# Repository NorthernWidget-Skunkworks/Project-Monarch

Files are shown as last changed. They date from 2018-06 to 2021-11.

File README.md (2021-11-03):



# Project-Monarch
Designs for a small scale and low cost pyronometer operating in both the short wave and long wave spectral regions

## Millable components

* [Pipe mount](https://easel.inventables.com/projects/cAirZefIUws53oghGYYopw). Accepts 1.25" to 3.25" innner diameter (ID) 1/4" (bolt diameter) U bolts. (1 1/8" U bolts are possible if you're willing to bend them.) Typical sizes available in the USA are 1.25", 1.5", 1.75", and 2".
* [Drilling jig](https://easel.inventables.com/projects/s-fOn9DWTmkeizO0vO8MGw) for Monarch box`

<br>
<br />This work is licensed under a <a rel="license" href="http://creativecommons.org/licenses/by-sa/4.0/">Creative Commons Attribution-ShareAlike 4.0 International License</a>.

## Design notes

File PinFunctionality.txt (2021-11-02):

Pin Functionality Monarch Short-Wave

Pin		Function
D0		Lux Int, Active Low
D1		Adc Int, Active Low
D7		Slave Address Select 
D3		Software SCL
D2		Software SDA

Function Explanation:

Lux Int:
Lux sensor (VEML6030) can be configured to output an interrupt for certian situations, this pin is native high (pull up), and it pulled low by the Lux sensor if an interrupt is triggered. Interrupt trigger must be configured by user.

Adc Int:				
ADC (ADS1115) can be configured to output an interrupt for certian situations, this pin is native high (pull up), and it pulled low by the ADC sensor if an interrupt is triggered (generally used to indicate a finished conversion). Interrupt trigger must be configured by user.

Slave Address Select:
This pin is used to select I2C device (if the device is the "top" or "bottom" device). This pin must be pulled up internally, and is natively floating (can be pulled up internally). This pin is an input, when the solder jumper on the board (J1) is jumped, this pin is pulled low, indicating the alternate device address should be used.

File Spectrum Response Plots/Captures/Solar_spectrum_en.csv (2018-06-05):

x | Curve1
204.85 | 0.1295
216.07 | 0.18429
225.9 | 0.23908
234.31 | 0.29387
242.73 | 0.34866
249.75 | 0.40574
255.36 | 0.46053
262.38 | 0.51761
269.39 | 0.5724
276.41 | 0.62948
282.02 | 0.68655
287.63 | 0.74135
294.65 | 0.79842
300.26 | 0.85322
307.27 | 0.91029
312.89 | 0.96737
319.9 | 1.02216
325.51 | 1.07924
332.53 | 1.13403
339.54 | 1.19111
346.56 | 1.2459
353.57 | 1.30298
360.59 | 1.35777
369.01 | 1.41256
377.43 | 1.46964
387.25 | 1.52443
398.47 | 1.5952
402.68 | 1.62716
412.5 | 1.64998
426.53 | 1.7002
439.16 | 1.73215
458.8 | 1.77779
486.87 | 1.80973
519.14 | 1.80741
531.76 | 1.79597
558.42 | 1.76169
582.27 | 1.71828
603.32 | 1.67258
622.96 | 1.62689
660.85 | 1.53095
679.09 | 1.48297
712.76 | 1.3916
731 | 1.34363
747.84 | 1.29565
766.08 | 1.24768
784.32 | 1.19971
798.38 | 1.16441
815.62 | 1.11836
836.39 | 1.07159
852.74 | 1.02698
870.86 | 0.99171
888.14 | 0.9507
910.59 | 0.90728
933.04 | 0.86159
955.49 | 0.81818
979.34 | 0.77705
996.18 | 0.74735
1020.03 | 0.70622
1045.29 | 0.66737
1071.94 | 0.62852
1097.2 | 0.59195
1111.23 | 0.57367
1137.89 | 0.53939
1167.35 | 0.5051
1196.82 | 0.47538
1226.28 | 0.44566
1255.75 | 0.41594
1288.02 | 0.39079
1318.88 | 0.36335
1351.15 | 0.34048
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

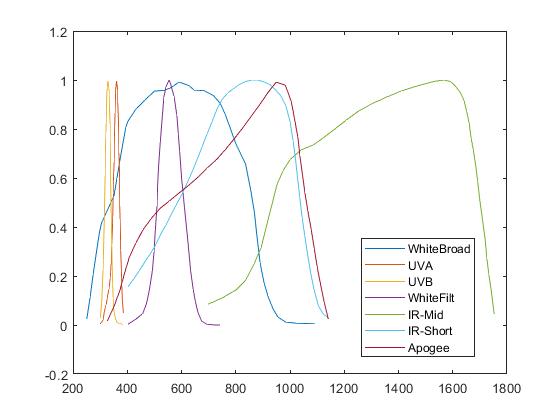
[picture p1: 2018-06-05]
Spectrum Response Plots/Spectrum.jpg

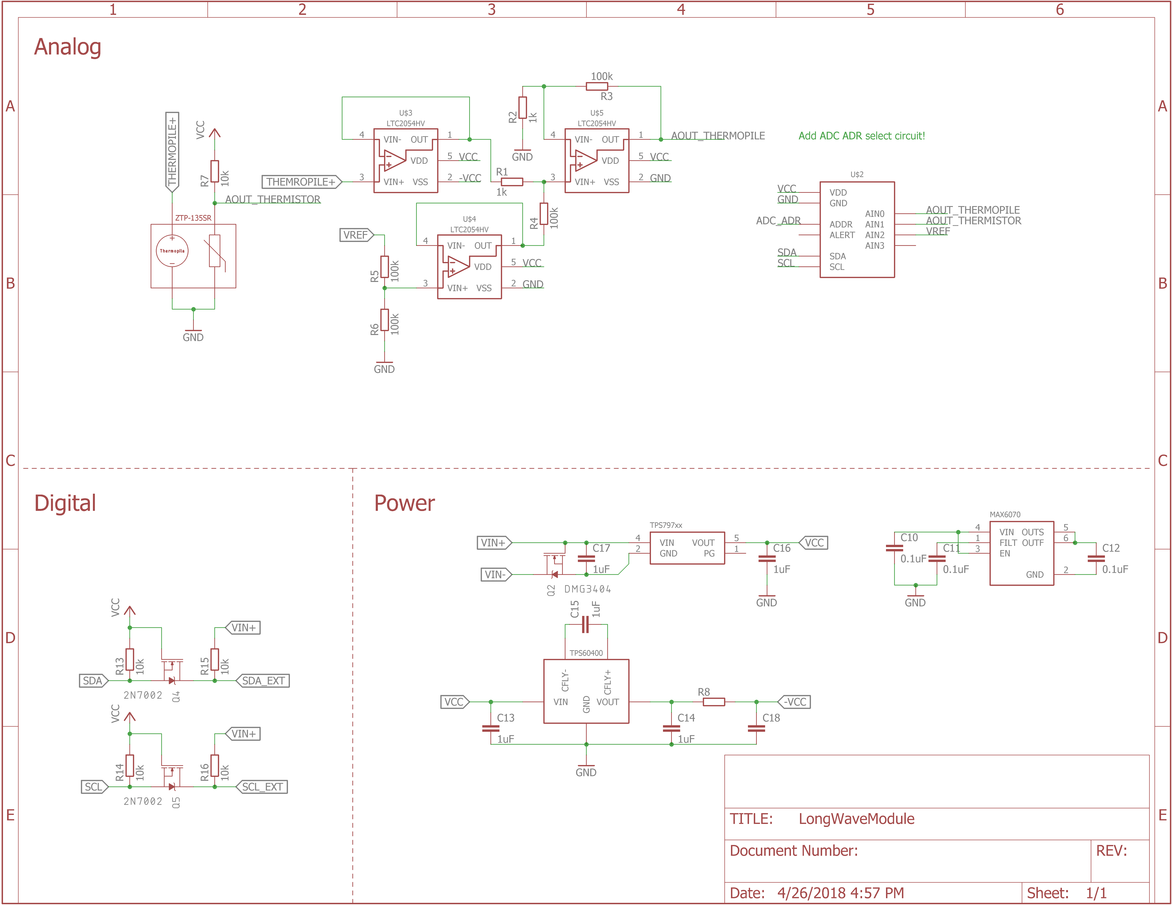
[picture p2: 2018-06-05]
Hardware/LongWaveSch.png

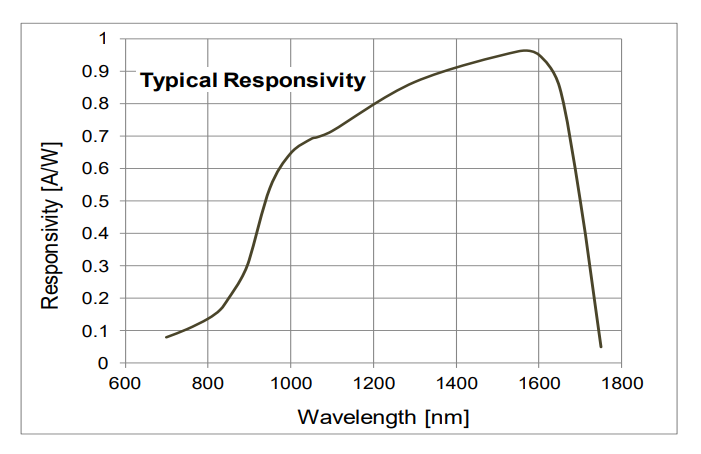
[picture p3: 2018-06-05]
Spectrum Response Plots/Captures/IR_MidWave_Response.png

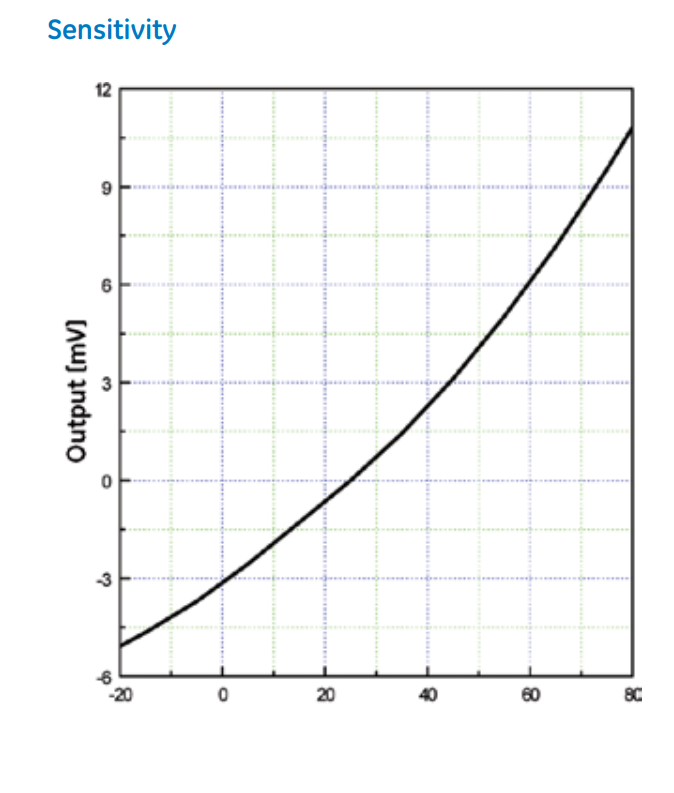
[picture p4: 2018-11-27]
Spectrum Response Plots/Captures/ZTP-135_Response.png

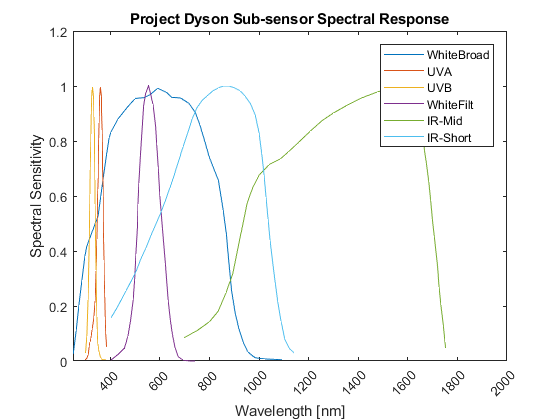
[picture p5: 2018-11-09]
Spectrum Response Plots/Spectrum.png

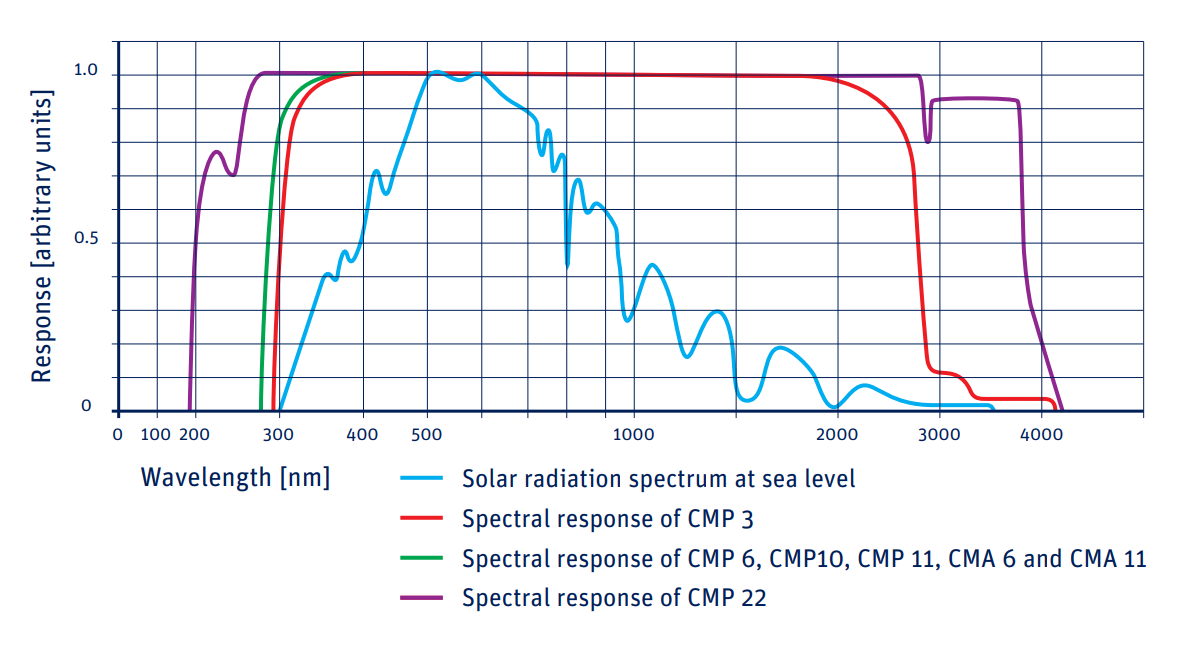
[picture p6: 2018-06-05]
Spectrum Response Plots/Captures/KippAndZonen_Response.png

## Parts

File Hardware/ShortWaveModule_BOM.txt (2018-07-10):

Partlist exported from C:/Users/You/Documents/Project-Dyson/Hardware/ShortWaveModule_SmallBoard.sch at 7/9/2018 9:44 AM

Qty Value                   Device                  Package              Parts                                         Description                                                                          DIGIKEY                DISP    MF                  MPN                PROD_ID     VALUE   VALUE_PART
2                           MOUNTING_HOLE4_NP       4_40                 H1, H2                                        Genaric Mechanical Mounting Hole                                                                                                                                                         
2   0.15uF                  C-EU0.15UFC0603         C0603                C2, C3                                        CAPACITOR, European symbol                                                           732-7990-1-ND                  Wurth               885012206072                                     
8   0.1uF                   C-EU0.1UFC0603          C0603                C4, C5, C8, C9, C10, C11, C12, C14            CAPACITOR, European symbol                                                           490-6051-1-ND                  Murata              GCM188R71E104KA57D                               
1   100k                    R-EU_P100KR0603         R0603                R4                                            RESISTOR, European symbol                                                            P100KDBCT-ND                   Panasonic           ERA-3AEB104V                           100k      
10  10k                     R-EU_10KR0603           R0603                R6, R7, R8, R11, R12, R13, R14, R15, R16, R18 RESISTOR, European symbol                                                            P10.0KHCT-ND                   Panasonic           ERJ-3EKF1002V                          10k       
1   10k                     R-EU_P10KR0603          R0603                R17                                           RESISTOR, European symbol                                                            P10KDBCT-ND                    Panasonic           ERA-3AEB103V                           10k       
1   10k                     R-EU_P10KR0603          R0603                R5                                            RESISTOR, European symbol                                                            P10KDBCT-ND                    Panasonic           ERA-3AEB103V                           10k       
1   10k                     THERMISTOR10K           R0603                RT1                                           Thermistor                                                                           490-16279-1-ND                 Murata              NCU18XH103F60RB                                  
1   10uF                    C-EU10UFC0805           C0805                C1                                            CAPACITOR, European symbol                                                           490-6473-6-ND                  Murata              GRM21BR61C106KE15K                               
4   1k                      R-EU_P1KR0603           R0603                R1, R2, R9, R10                               RESISTOR, European symbol                                                            P1.0KDBCT-ND                   Panasonic           ERA-3AEB102V                           1k        
4   1uF                     C-EU1UFC0603            C0603                C6, C7, C13, C15                              CAPACITOR, European symbol                                                           1276-6524-1-ND                 Samsung             1276-6524-1-ND                                   
1   27R                     R-EU_27R0603            R0603                R3                                            RESISTOR, European symbol                                                            311-27.0HRCT-ND                Yageo               RC0603FR-0727RL                        27        
2   2N7002                  MOSFET-NCH-2N7002PW     SOT323               Q1, Q2                                        N-channel MOSFETs                                                                    2N7002W-FDICT-ND               Diodes Incorporated 2N7002W-7-F        TRANS-11151 2N7002            
1   ADS1115                 ADS1115                 VSSOP_10             U5                                            ADS1115 - Sigma Delta ADC                                                            296-38849-1-ND                 TI                  ADS1115IDGSR                                     
1   ADXL343                 ADXL343                 LGA-14               U1                                            ADXL343 - Digital Accelerometer(I2C/SPI)                                             ADXL343BCCZ-ND                 Analog Devices      ADXL343BCCZ                                      
1   ATTINY441/841841        ATTINY441/841841        SOIC_14              U2                                            ATTINY441, ATTINY841 8 bit MCU, 4/8k flash, 256/512B SRAM                            ATTINY841-SSU-ND               Atmel               ATTINY841-SSU                                    
1   AVRISP-6                AVRISP-6                AVRISP               ISP1                                          AVR ISP HEADER                                                                                                                                                                           
3   CONN_42.54              CONN_42.54              1X04                 J2, J3, J4                                    Genaric 4 pin connector                                                                                                                                                                  
1   CONN_42.54_SCREW        CONN_42.54_SCREW        1X04_SCREW           J1                                            Genaric 4 pin connector                                                              ED10563-ND                     On Shore            OSTVN04A150                                      
1   DMG3404                 MOSFET-NCH-DMG3404L     SOT23-3              Q3                                            N-channel MOSFETs                                                                    DMG3404L-7DICT-ND              Diodes Incorporated DMG3404L-7                     DMG3404           
2   JUMPER-SMT_2_NO_SILK    JUMPER-SMT_2_NO_SILK    SMT-JUMPER_2_NO_SILK JP1, JP2                                      Normally open jumper                                                                                                                                                                     
2   LTC2054                 LTC2054                 SOT23-5              U3, U4                                        LTC2054 -Single Micropower Zero Drift Op-Amp                                         LTC2054HS5#TRMPBFCT-ND LTC2054 LT                  LTC2054HS5#TRMPBF                                
1   PHOTODIODESD003-151-001 PHOTODIODESD003-151-001 D1206                D1                                            Photodiode                                                                           SD003-151-001CT-ND             Luna Opto           SD003-151-001                                    
1   PHOTODIODEVEMD1060      PHOTODIODEVEMD1060      D0805                D2                                            Photodiode                                                                           VEMD1060X01CT-ND               Vishay              VEMD1060X01                                      
1   TPS79733                TPS79733                DCK_R-PDSO-G5        U6                                            TPS797xx, Ultra low power linear voltage regulator, fixed voltages of 1.8v, 3v, 3.3v 296-11990-1-ND                 TI                  TPS79733DCKR                                     
1   VEML6030                VEML6030                VEML6030             U7                                            VEML6030 - Ambient Light Sensor with I2C Interface                                   VEML6030-GS15CT-ND             Vishay              VEML6030-GS15                                    
1   VEML6075                VEML6075                VEML6075             U8                                            VEML6075 - UVA and UVB Light Sensor with I2C Interface                               VEML6075CT-ND                  Vishay              VEML6075

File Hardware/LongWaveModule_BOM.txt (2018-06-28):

Partlist exported from C:/Users/You/Documents/Project-Dyson/Hardware/LongWaveModule.sch at 6/28/2018 1:53 PM

Qty Value                        Device                       Package                      Parts                          Description                                                                          DIGIKEY                 DISP      MF                  MPN                PROD_ID     VALUE   VALUE_PART
7   0.1uF                        C-EU0.1UFC0603               C0603                        C5, C6, C9, C10, C11, C12, C13 CAPACITOR, European symbol                                                           490-6051-1-ND                     Murata              GCM188R71E104KA57D                               
4   100k                         R-EU_P100KR0603              R0603                        R6, R7, R10, R11               RESISTOR, European symbol                                                            P100KDBCT-ND                      Panasonic           ERA-3AEB104V                           100k      
4   10k                          R-EU_10KR0603                R0603                        R1, R2, R4, R5                 RESISTOR, European symbol                                                            P10.0KHCT-ND                      Panasonic           ERJ-3EKF1002V                          10k       
1   10k                          R-EU_P10KR0603               R0603                        R3                             RESISTOR, European symbol                                                            P10KDBCT-ND                       Panasonic           ERA-3AEB103V                           10k       
1   1k                           R-EU_1KR0603                 R0603                        R12                            RESISTOR, European symbol                                                            311-1KLDCT-ND                     Yageo               AC0603FR-071KL                         1k        
2   1k                           R-EU_P1KR0603                R0603                        R8, R9                         RESISTOR, European symbol                                                            P1.0KDBCT-ND                      Panasonic           ERA-3AEB102V                           1k        
6   1uF                          C-EU1UFC0603                 C0603                        C1, C2, C3, C4, C7, C8         CAPACITOR, European symbol                                                           1276-6524-1-ND                    Samsung             1276-6524-1-ND                                   
3   2-56                         MOUNTING_HOLE2_NP            2_56                         H1, H2, H3                     Genaric Mechanical Mounting Hole                                                                                                                                                            
2   2N7002                       MOSFET-NCH-2N7002PW          SOT323                       Q1, Q2                         N-channel MOSFETs                                                                    2N7002W-FDICT-ND                  Diodes Incorporated 2N7002W-7-F        TRANS-11151 2N7002            
1   ADS1115                      ADS1115                      VSSOP_10                     U7                             ADS1115 - Sigma Delta ADC                                                            296-38849-1-ND                    TI                  ADS1115IDGSR                                     
1   CONN_42.54_SCREW             CONN_42.54_SCREW             1X04_SCREW                   J1                             Genaric 4 pin connector                                                              ED10563-ND                        On Shore            OSTVN04A150                                      
1   DMG3404                      MOSFET-NCH-DMG3404L          SOT23-3                      Q3                             N-channel MOSFETs                                                                    DMG3404L-7DICT-ND                 Diodes Incorporated DMG3404L-7                     DMG3404           
1   JUMPER-SMT_3_1-NC_PASTE_SILK JUMPER-SMT_3_1-NC_PASTE_SILK SMT-JUMPER_3_1-NC_PASTE_SILK JP1                            Normally closed solder jumper (1 of 2 connections)                                                                                                                                          
1   LTC2050HV                    LTC2050HV                    SOT23-5                      U2                             LTC2050 -Single Micropower Zero Drift Op-Amp                                         LTC2050HVIS5#TRPBFCT-ND LTC2050HV LT                  LTC2050HVIS5#TRPBF                               
2   LTC2054                      LTC2054                      SOT23-5                      U3, U4                         LTC2054 -Single Micropower Zero Drift Op-Amp                                         LTC2054HS5#TRMPBFCT-ND  LTC2054   LT                  LTC2054HS5#TRMPBF                                
1   MAX6070AAUT18                MAX6070AAUT18                SOT23-6L                     U8                             MAX6070 Low Noise high precision voltage referance                                   MAX6070BAUT18+TCT-ND              Maxim               MAX6070BAUT18+T                                  
1   STP-135SR                    STP-135SR                    TO-46                        U1                             ZTP-135SR - Thermopile Temp Sensor with integrated thermistor                        235-1330-ND                       Amphenol            ZTP-135SR                                        
1   TPS60403                     TPS60403                     SOT23-5                      U5                             TPS6040x - Unregulated Charge Pump Voltage Inverter                                  296-27005-1-ND                    TI                  TPS60403DBVR                                     
1   TPS79733                     TPS79733                     DCK_R-PDSO-G5                U6                             TPS797xx, Ultra low power linear voltage regulator, fixed voltages of 1.8v, 3v, 3.3v 296-11990-1-ND                    TI                  TPS79733DCKR

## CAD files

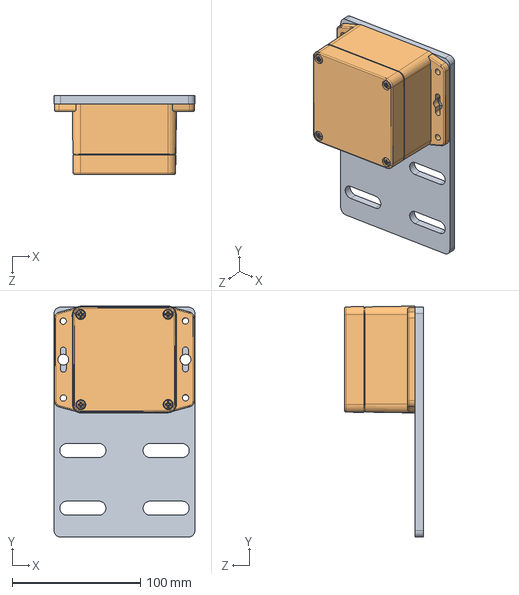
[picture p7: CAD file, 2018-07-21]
PipeMount.SLDASM
110.0 x 180.3 x 61.5 mm
PipeMount
W_-31F1

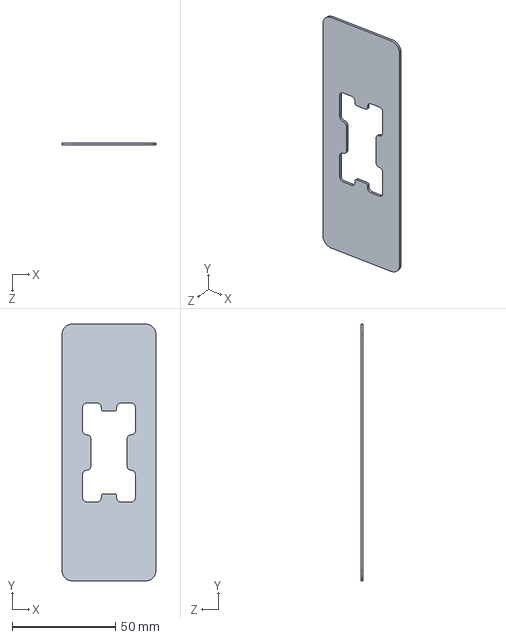
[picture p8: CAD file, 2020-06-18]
3Dprint/StencilMount_MonarchLW.SLDPRT
45.5 x 124.4 x 1.20 mm

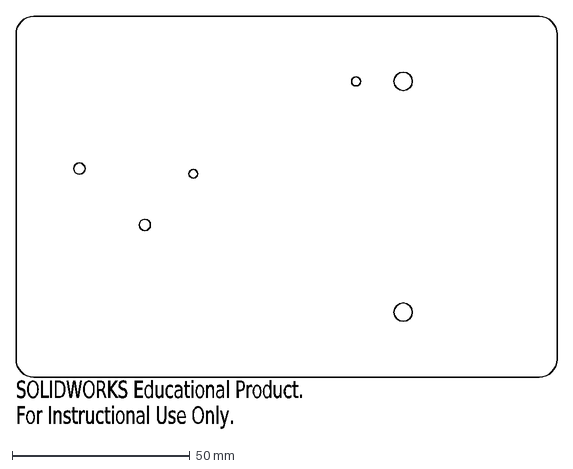
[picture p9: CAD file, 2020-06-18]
CNC/TestWith_KippZonen/PyroTestingPlate.DXF
SOLIDWORKS Educational Product.
For Instructional Use Only.

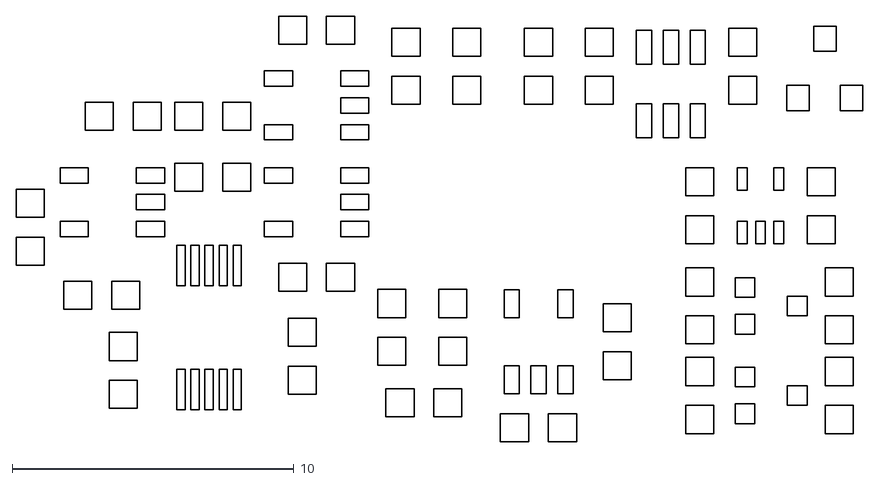
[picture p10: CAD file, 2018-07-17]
Hardware/Stencil.dxf
30.0 x 15.1

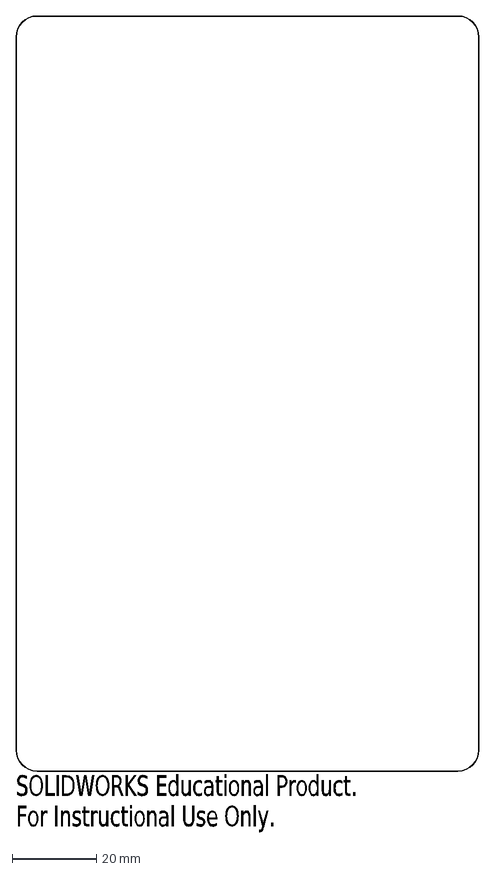
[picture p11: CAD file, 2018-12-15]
PipeMount_Outline.DXF
SOLIDWORKS Educational Product.
For Instructional Use Only.

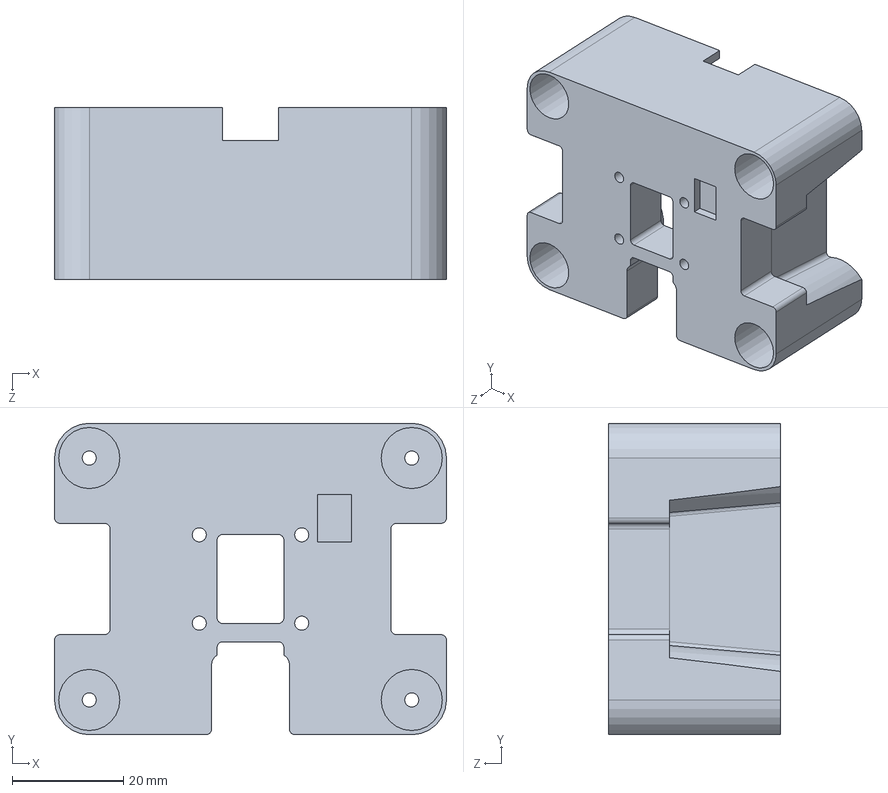
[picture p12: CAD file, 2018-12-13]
BoardCaseMount_DesicantHolders.SLDPRT
70.5 x 56.0 x 31.0 mm

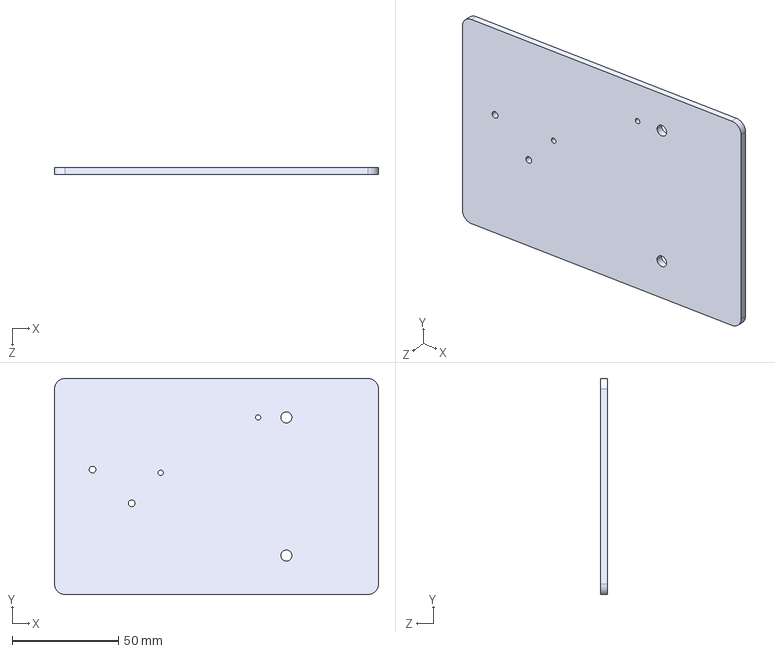
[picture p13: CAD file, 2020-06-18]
CNC/TestWith_KippZonen/PyroTestingBoard.STEP
152.4 x 101.6 x 3.17 mm

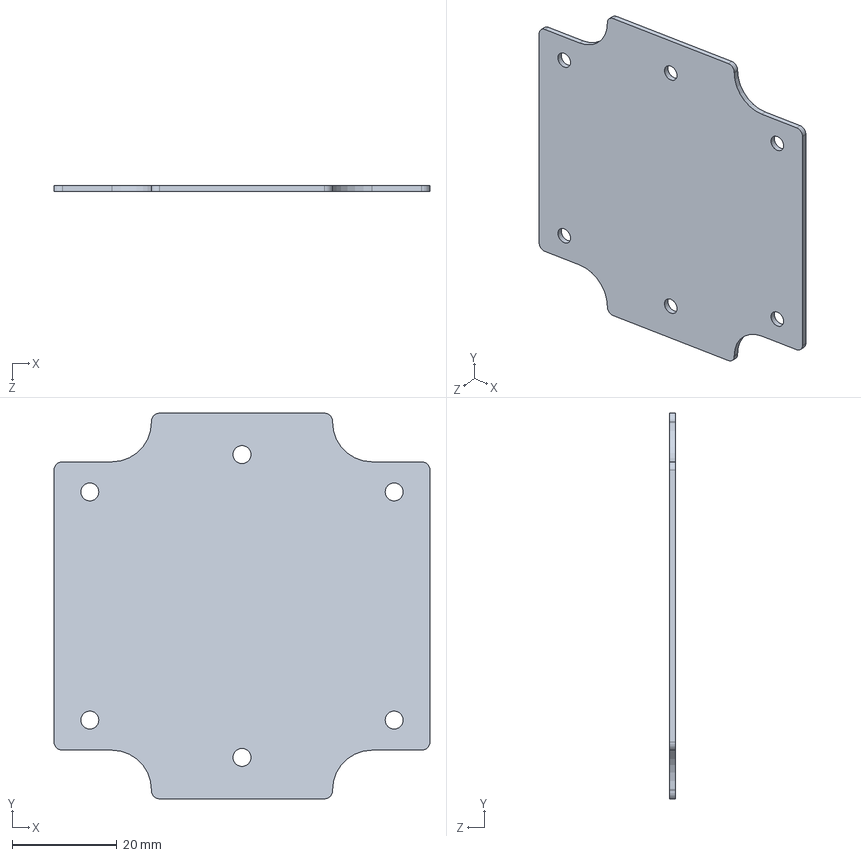
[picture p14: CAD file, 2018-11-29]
WP-31_InternalMountPlate.SLDPRT
71.7 x 73.6 x 1.20 mm

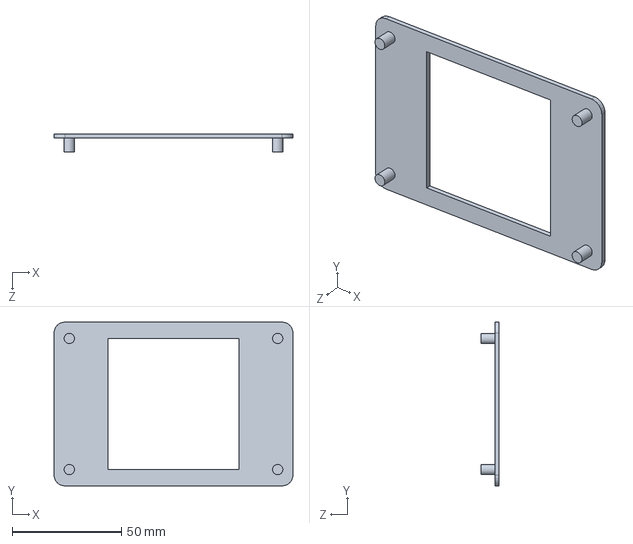
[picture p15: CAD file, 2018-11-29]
DiffuserGuide_BOTTOM.SLDPRT
109.4 x 75.0 x 8.35 mm

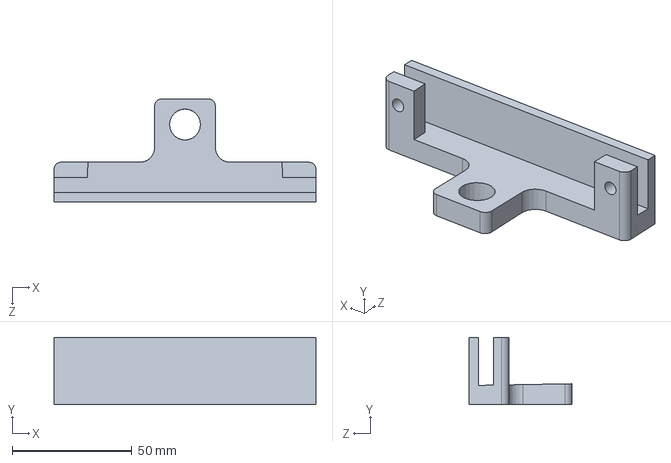
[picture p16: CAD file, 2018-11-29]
DrillGuide.SLDPRT
109.4 x 28.0 x 43.1 mm

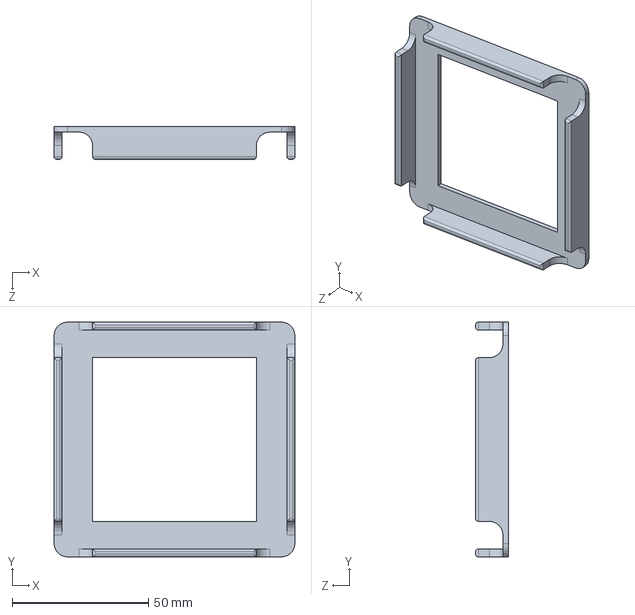
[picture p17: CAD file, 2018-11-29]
DiffuserGuide_TOP.SLDPRT
88.4 x 86.1 x 12.0 mm

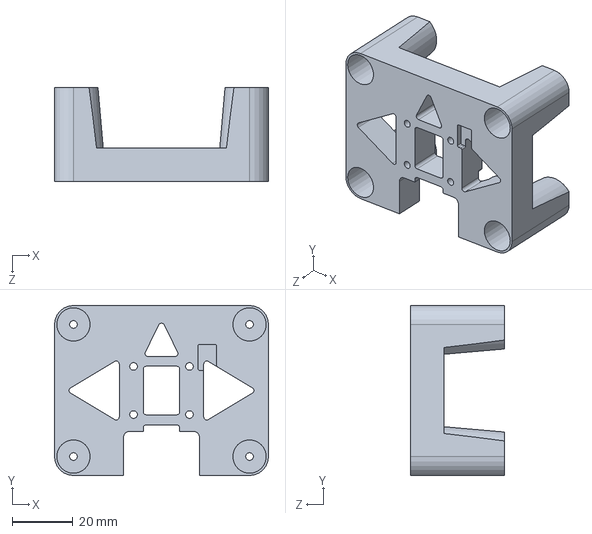
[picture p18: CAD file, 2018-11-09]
BoardCaseMount.SLDPRT
70.5 x 56.0 x 31.0 mm

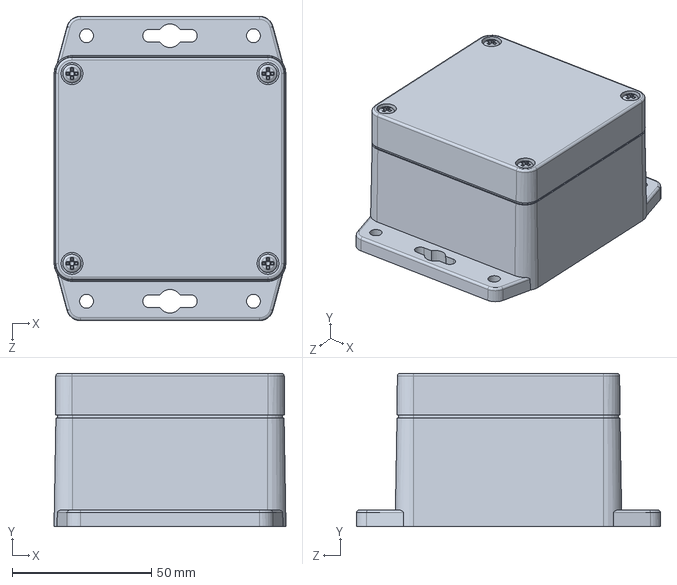
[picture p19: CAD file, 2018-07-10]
W_-31F1.SLDPRT
83.4 x 55.1 x 109.4 mm

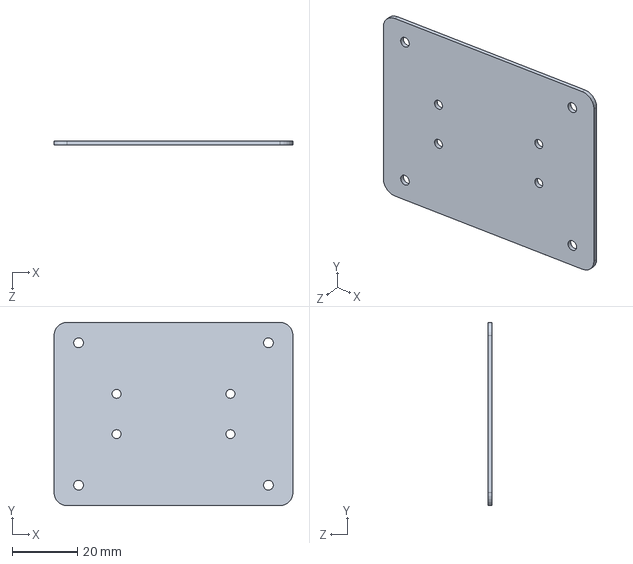
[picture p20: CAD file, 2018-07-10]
LongWaveMountPlate.SLDPRT
73.0 x 56.0 x 1.20 mm

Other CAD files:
Hardware/LongWaveModule-tcream.dxf
Hardware/LongWaveModule-bcream.dxf
LongWaveMountPlate_v1.SLDPRT
3Dprint/StencilMount_MonarchLW.STL
BoardCaseMount.STL
BoardCaseMount_DesicantHolders.STL
CNC/TestWith_KippZonen/PyroTestingBoard.SLDPRT
CNC/TestWith_KippZonen/PyroTestingBoard.STL
DiffuserGuide_BOTTOM.STL
DiffuserGuide_TOP.STL
DrillGuide.STL
LongWaveMountPlate.STL
LongWaveMountPlate_v1.STL
PipeMount.DXF
PipeMount.SLDPRT

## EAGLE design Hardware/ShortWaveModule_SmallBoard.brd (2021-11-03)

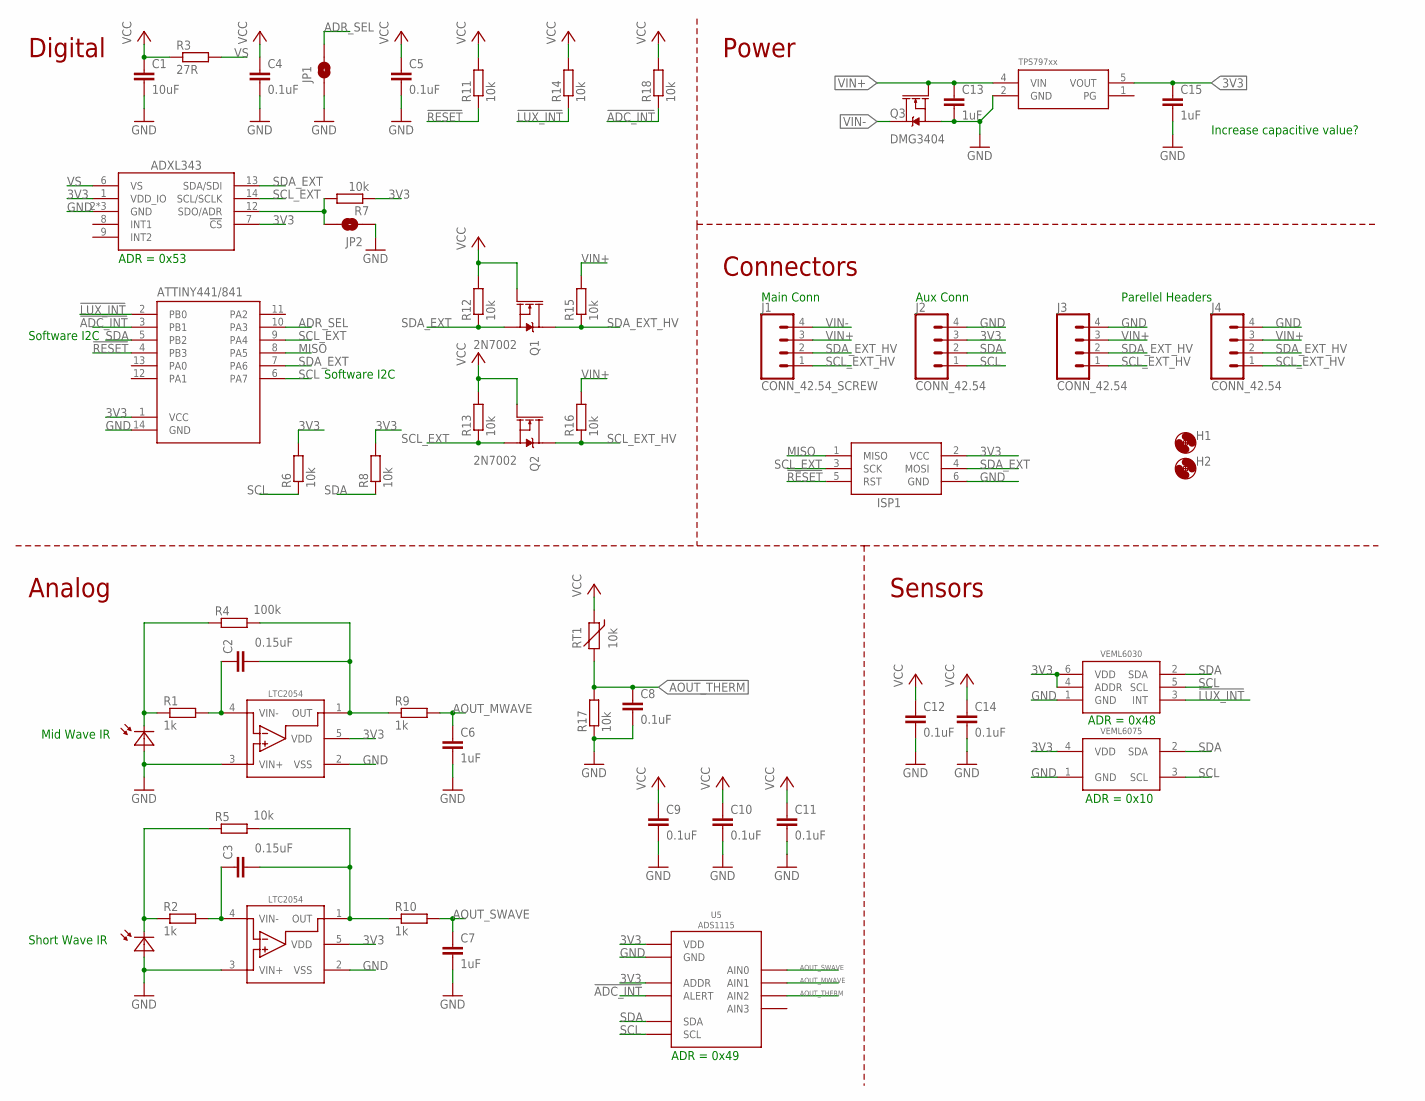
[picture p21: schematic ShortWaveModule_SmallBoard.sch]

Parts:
C1: 10uF; C0805
C2, C3: 0.15uF; C0603
C4, C5, C8, C9, C10, C11, C12, C14: 0.1uF; C0603
C6, C7, C13, C15: 1uF; C0603
D1: PHOTODIODESD003-151-001; D1206
D2: PHOTODIODEVEMD1060; D0805
H1, H2: MOUNTING_HOLE4_NP; 4_40
ISP1: AVRISP-6; AVRISP
J1: CONN_42.54_SCREW; 1X04_SCREW
J2, J3, J4: CONN_42.54; 1X04
JP1, JP2: JUMPER-SMT_2_NO_SILK; SMT-JUMPER_2_NO_SILK
Q1, Q2: 2N7002; SOT323
Q3: DMG3404; SOT23-3
R1, R2, R9, R10: 1k; R0603
R3: 27R; R0603
R4: 100k; R0603
R5, R6, R7, R8, R11, R12, R13, R14, R15, R16, R18: 10k; R0603
R17: 10k; R0603; MPN ERA-3AEB103V; DIGIKEY P10KDBCT-ND
RT1: 10k; R0603
U1: ADXL343; LGA-14
U2: ATTINY441/841841; SOIC_14
U3, U4: LTC2054; SOT23-5
U5: ADS1115; VSSOP_10
U6: TPS79733; DCK_R-PDSO-G5
U7: VEML6030
U8: VEML6075

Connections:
3V3: C1.1, C4.1, C5.1, C9.1, C10.1, C11.1, C12.1, C14.1, C15.1, ISP1.2 (VCC), J2.3, Q1.1 (G), Q2.1 (G), R3.1, R6.2, R7.1, R8.2, R11.2, R12.2, R13.2, R14.2, R18.2, RT1.1 (2), U1.1 (VDD_IO), U1.7 (!CS), U2.1 (VCC), U3.5 (VDD), U4.5 (VDD), U5.1 (ADDR), U5.8 (VDD), U6.5 (VOUT), U7.4 (ADDR), U7.6 (VDD), U8.4 (VDD)
!ADC_INT: R18.1, U2.3 (PB1), U5.2 (ALERT)
!LUX_INT: R14.1, U2.2 (PB0), U7.3 (INT)
!RESET: ISP1.5 (RST), R11.1, U2.4 (PB3)
ADR_SEL: JP1.2, U2.10 (PA3)
AOUT_MWAVE: C6.1, R9.2, U5.5 (AIN1)
AOUT_SWAVE: C7.1, R10.2, U5.4 (AIN0)
AOUT_THERM: C8.1, R17.2, RT1.2 (1), U5.6 (AIN2)
GND: C1.2, C4.2, C5.2, C6.2, C7.2, C8.2, C9.2, C10.2, C11.2, C12.2, C13.2, C14.2, C15.2, D1.A, D2.A, ISP1.6 (GND), J2.4, J3.4, J4.4, JP1.1, JP2.1, Q3.2 (S), R17.1, U1.2 (GND), U1.4 (GND), U1.5 (GND), U2.14 (GND), U3.2 (VSS), U3.3 (VIN+), U4.2 (VSS), U4.3 (VIN+), U5.3 (GND), U6.2 (GND), U7.1 (GND), U8.1 (GND)
MISO: ISP1.1 (MISO), U2.8 (PA5)
unnamed: JP2.2, R7.2, U1.12 (SDO/ADR)
unnamed: C3.1, R2.2, U4.4 (VIN-)
unnamed: D2.C, R2.1, R5.1
unnamed: D1.C, R1.1, R4.1
unnamed: C2.1, R1.2, U3.4 (VIN-)
unnamed: C2.2, R4.2, R9.1, U3.1 (OUT)
unnamed: C3.2, R5.2, R10.1, U4.1 (OUT)
SCL: J2.1, R6.1, U2.6 (PA7), U5.10 (SCL), U7.5 (SCL), U8.3 (SCL)
SCL_EXT: ISP1.3 (SCK), Q2.2 (S), R13.1, U1.14 (SCL/SCLK), U2.9 (PA4)
SCL_EXT_HV: J1.1, J3.1, J4.1, Q2.3 (D), R16.1
SDA: J2.2, R8.1, U2.5 (PB2), U5.9 (SDA), U7.2 (SDA), U8.2 (SDA)
SDA_EXT: ISP1.4 (MOSI), Q1.2 (S), R12.1, U1.13 (SDA/SDI), U2.7 (PA6)
SDA_EXT_HV: J1.2, J3.2, J4.2, Q1.3 (D), R15.1
VIN+: C13.1, J1.3, J3.3, J4.3, Q3.1 (G), R15.2, R16.2, U6.4 (VIN)
VIN-: J1.4, Q3.3 (D)
VS: R3.2, U1.6 (VS)

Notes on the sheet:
Software I2C
ADR = 0x48
ADR = 0x10
ADR = 0x49
Increase capacitive value?
Digital
Sensors
Power
Analog
Short Wave IR
Mid Wave IR
Connectors
Main Conn
Aux Conn
Parellel Headers
ADR = 0x53

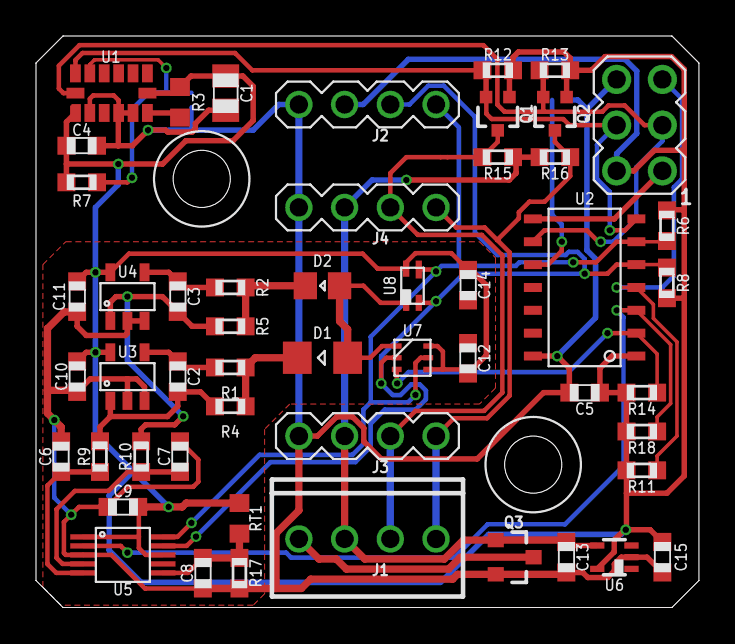
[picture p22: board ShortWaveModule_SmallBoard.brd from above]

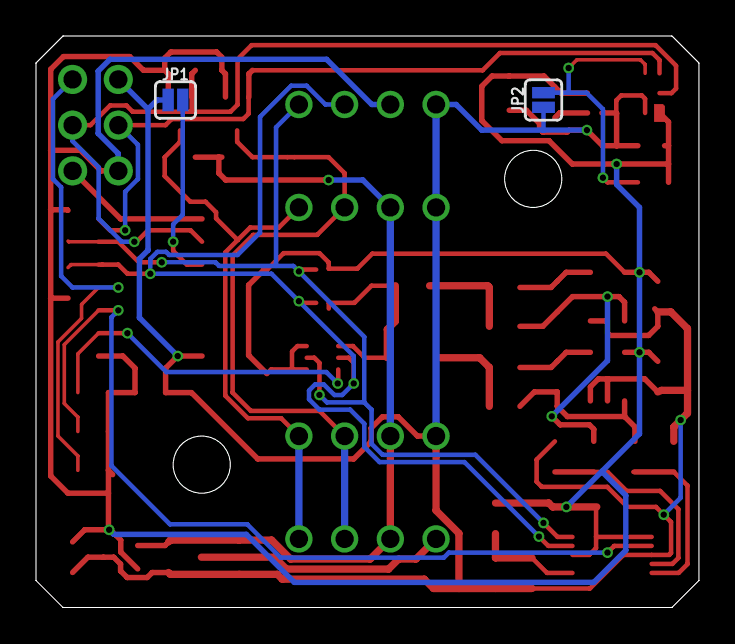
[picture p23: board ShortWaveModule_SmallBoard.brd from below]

Board: 2 copper layers, 36.8 x 31.8 mm, 56 parts (2 on the bottom side), 26 nets.

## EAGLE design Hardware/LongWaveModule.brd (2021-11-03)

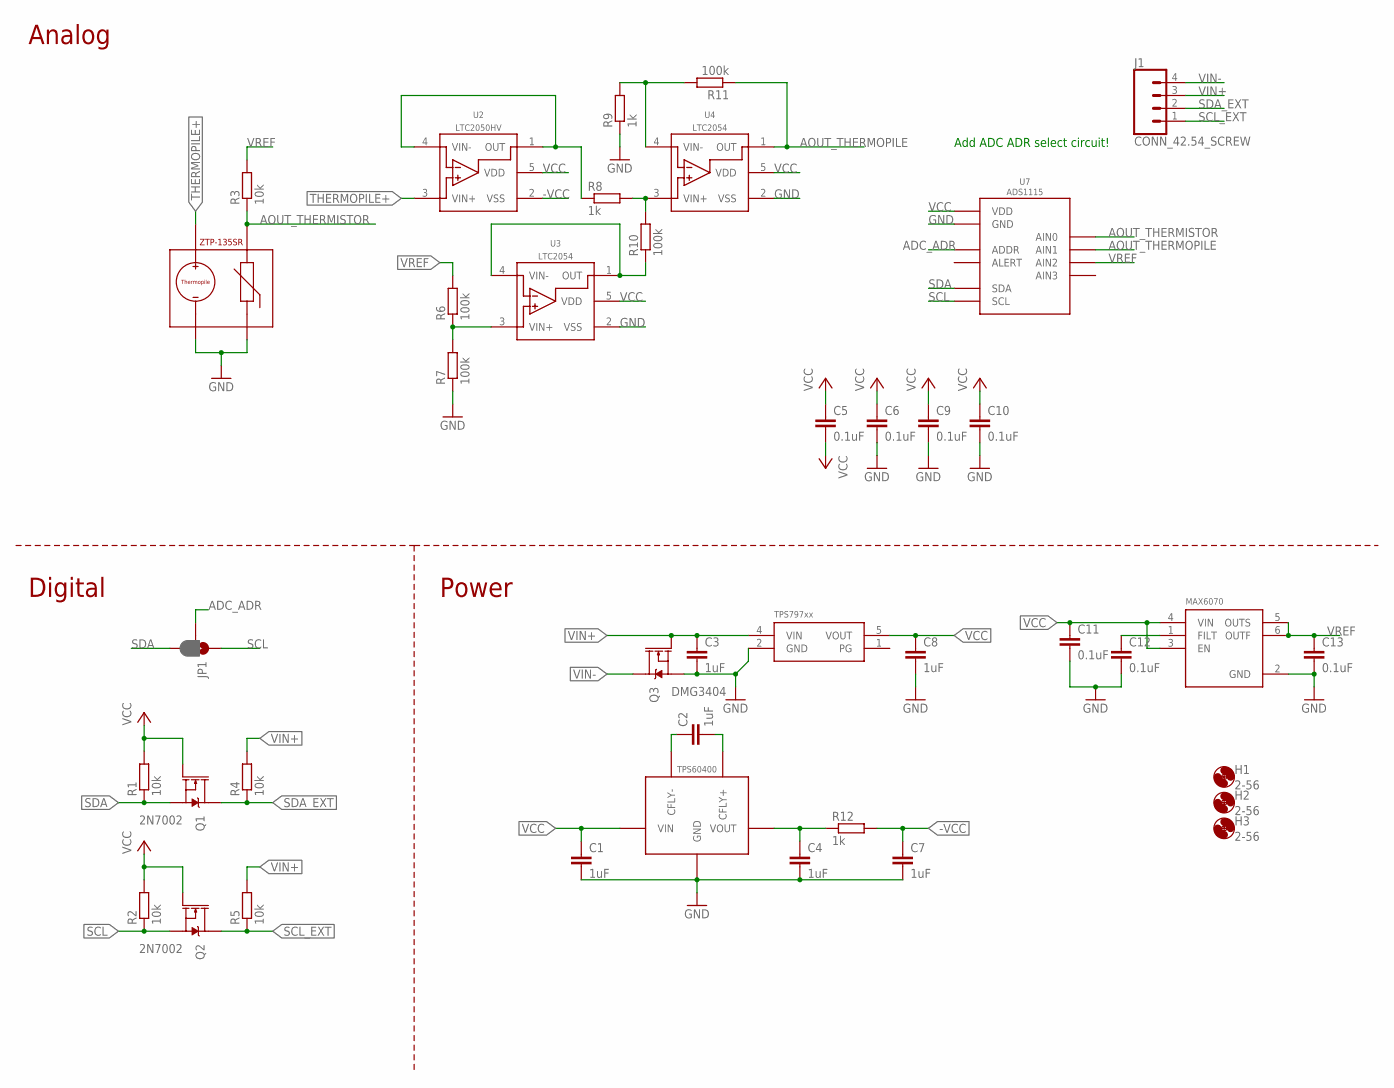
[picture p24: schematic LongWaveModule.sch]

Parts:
C1, C2, C3, C4, C7, C8: 1uF; C0603
C5, C6, C9, C10, C11, C12, C13: 0.1uF; C0603
H1, H2, H3: 2-56; 2_56
J1: CONN_42.54_SCREW; 1X04_SCREW
JP1: JUMPER-SMT_3_1-NC_PASTE_SILK; SMT-JUMPER_3_1-NC_PASTE_SILK
Q1, Q2: 2N7002; SOT323
Q3: DMG3404; SOT23-3
R1, R2, R3, R4, R5: 10k; R0603
R6, R7, R10, R11: 100k; R0603
R8, R9, R12: 1k; R0603
U1: STP-135SR; TO-46
U2: LTC2050HV; SOT23-5
U3, U4: LTC2054; SOT23-5
U5: TPS60403; SOT23-5
U6: TPS79733; DCK_R-PDSO-G5
U7: ADS1115; VSSOP_10
U8: MAX6070AAUT18; SOT23-6L

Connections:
-VCC: C5.2, C7.1, R12.2, U2.2 (VSS)
ADC_ADR: JP1.2, U7.1 (ADDR)
AOUT_THERMISTOR: R3.1, U1.THERMISTOR+, U7.4 (AIN0)
AOUT_THERMOPILE: R11.1, U4.1 (OUT), U7.5 (AIN1)
GND: C1.2, C3.2, C4.2, C6.2, C7.2, C8.2, C9.2, C10.2, C11.2, C12.2, C13.2, Q3.2 (S), R7.1, R9.1, U1.THERMISTOR_GND (THERMISTOR-), U1.THERMOPILE_GND (THEMROPILE-), U3.2 (VSS), U4.2 (VSS), U5.4 (GND), U6.2 (GND), U7.3 (GND), U8.2 (GND)
unnamed: R8.1, U2.1 (OUT), U2.4 (VIN-)
unnamed: R8.2, R10.2, U4.3 (VIN+)
unnamed: R9.2, R11.2, U4.4 (VIN-)
unnamed: R10.1, U3.1 (OUT), U3.4 (VIN-)
unnamed: R6.1, R7.2, U3.3 (VIN+)
unnamed: C12.1, U8.1 (FILT)
unnamed: C2.1, U5.3 (CFLY-)
unnamed: C2.2, U5.5 (CFLY+)
unnamed: C4.1, R12.1, U5.1 (VOUT)
SCL: JP1.1, Q2.2 (S), R2.1, U7.10 (SCL)
SCL_EXT: J1.1, Q2.3 (D), R5.1
SDA: JP1.3, Q1.2 (S), R1.1, U7.9 (SDA)
SDA_EXT: J1.2, Q1.3 (D), R4.1
THERMOPILE+: U1.THERMOPILE+, U2.3 (VIN+)
VCC: C1.1, C5.1, C6.1, C8.1, C9.1, C10.1, C11.1, Q1.1 (G), Q2.1 (G), R1.2, R2.2, U2.5 (VDD), U3.5 (VDD), U4.5 (VDD), U5.2 (VIN), U6.5 (VOUT), U7.8 (VDD), U8.3 (EN), U8.4 (VIN)
VIN+: C3.1, J1.3, Q3.1 (G), R4.2, R5.2, U6.4 (VIN)
VIN-: J1.4, Q3.3 (D)
VREF: C13.1, R3.2, R6.2, U7.6 (AIN2), U8.5 (OUTS), U8.6 (OUTF)

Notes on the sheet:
Add ADC ADR select circuit!
Analog
Digital
Power

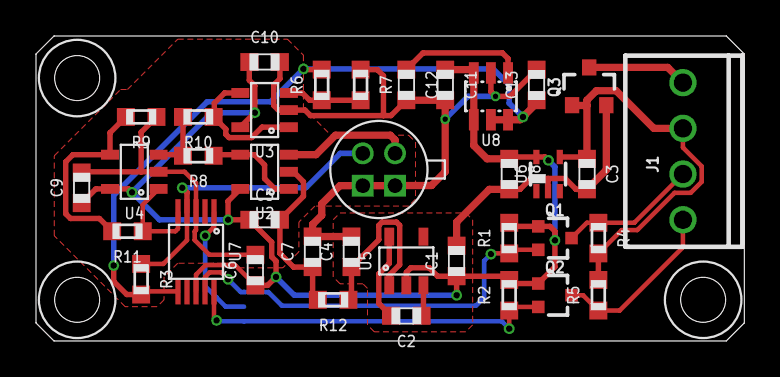
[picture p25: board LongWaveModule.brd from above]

Board: 2 copper layers, 39.4 x 16.9 mm, 41 parts (1 on the bottom side), 23 nets.

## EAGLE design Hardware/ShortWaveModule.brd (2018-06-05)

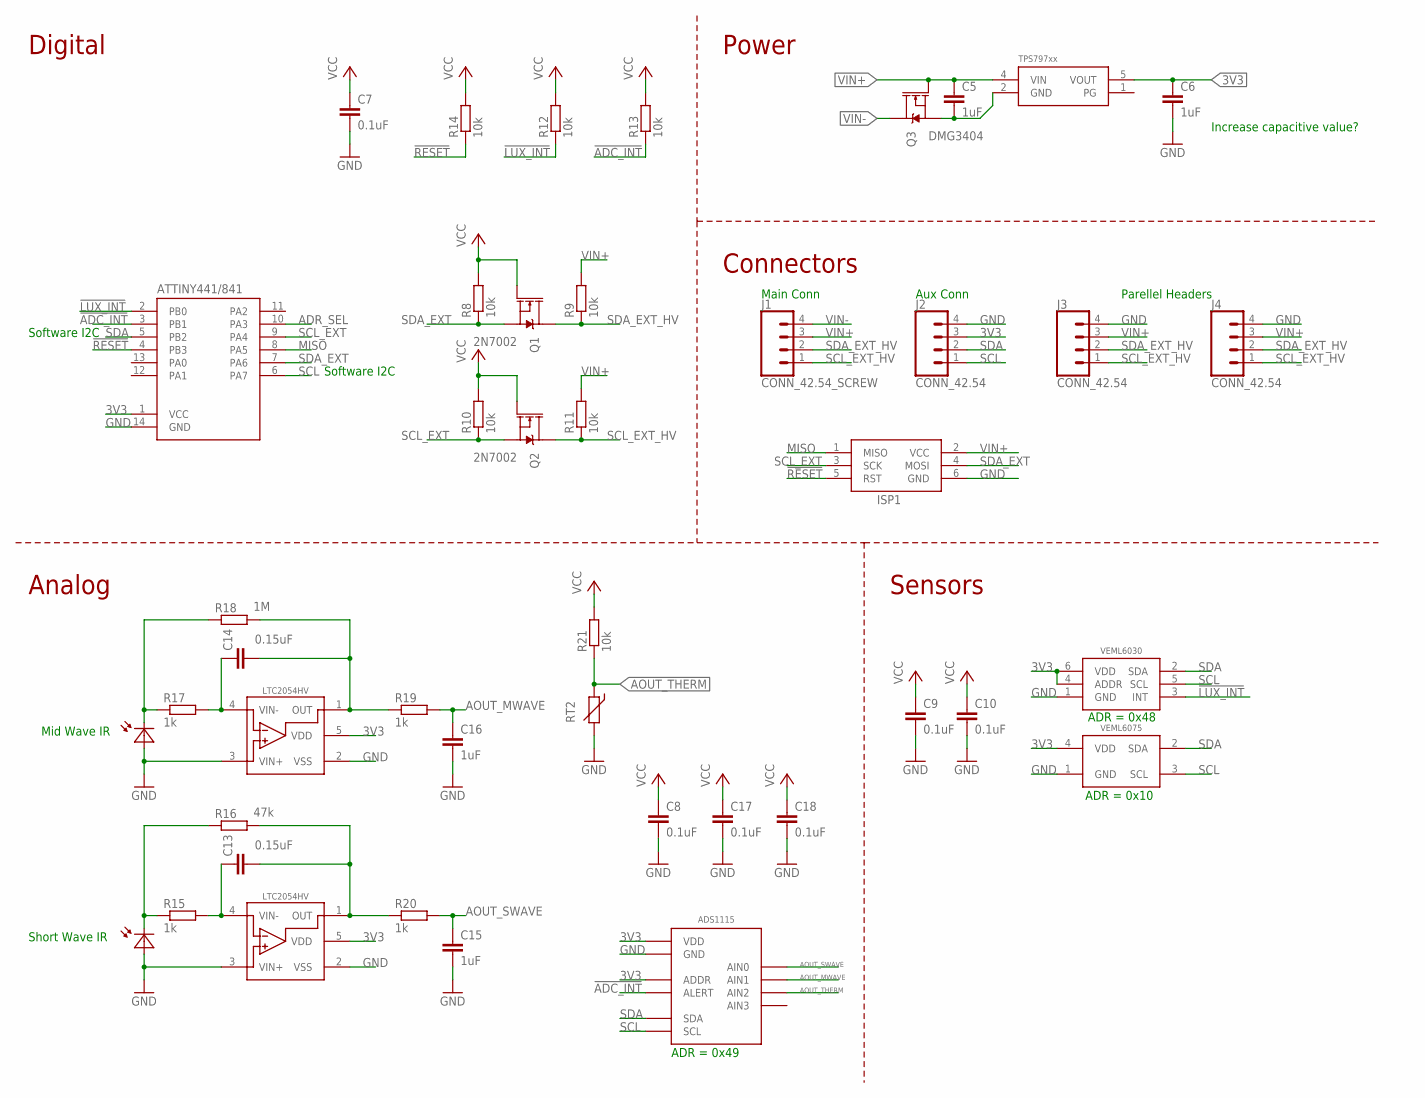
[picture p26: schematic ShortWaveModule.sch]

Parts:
ADS1115: ADS1115; VSSOP_10
C5, C6, C15, C16: 1uF; C0603
C7, C8, C9, C10, C17, C18: 0.1uF; C0603
C13, C14: 0.15uF; C0603
ISP1: AVRISP-6; AVRISP
J1: CONN_42.54_SCREW; 1X04_SCREW
J2, J3, J4: CONN_42.54; 1X04
Q1, Q2: 2N7002; SOT323
Q3: DMG3404; SOT23-3
R8, R9, R10, R11, R12, R13, R14, R21: 10k; R0603
R15, R17, R19, R20: 1k; R0603
R16: 47k; R0603
R18: 1M; R0603
RT2: THERMISTOR10K; R0603
U$1: ATTINY441/841841; SOIC_14
U$2: VEML6030
U$3: VEML6075
U$5: TPS79733; DCK_R-PDSO-G5
U$9: PHOTODIODEMTD5010W; TO-18
U$10: PHOTODIODESD003-151-001; D1206
U$11, U$12: LTC2054HV; SOT23-5

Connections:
3V3: ADS1115.1 (ADDR), ADS1115.8 (VDD), C6.1, C7.1, C8.1, C9.1, C10.1, C17.1, C18.1, J2.3, Q1.1 (G), Q2.1 (G), R8.2, R10.2, R12.2, R13.2, R14.2, R21.2, U$1.1 (VCC), U$2.4 (ADDR), U$2.6 (VDD), U$3.4 (VDD), U$5.5 (VOUT), U$11.5 (VDD), U$12.5 (VDD)
!ADC_INT: ADS1115.2 (ALERT), R13.1, U$1.3 (PB1)
!LUX_INT: R12.1, U$1.2 (PB0), U$2.3 (INT)
!RESET: ISP1.5 (RST), R14.1, U$1.4 (PB3)
ADR_SEL: U$1.10 (PA3)
AOUT_MWAVE: ADS1115.5 (AIN1), C14.2, R18.2, R19.1, U$11.1 (OUT)
AOUT_SWAVE: ADS1115.4 (AIN0), C13.2, R16.2, R20.1, U$12.1 (OUT)
AOUT_THERM: ADS1115.6 (AIN2), R21.1, RT2.1
GND: ADS1115.3 (GND), C6.2, C7.2, C8.2, C9.2, C10.2, C15.2, C16.2, C17.2, C18.2, ISP1.6 (GND), J2.4, J3.4, J4.4, RT2.2, U$1.14 (GND), U$2.1 (GND), U$3.1 (GND), U$9.ANODE (A), U$10.A, U$11.2 (VSS), U$11.3 (VIN+), U$12.2 (VSS), U$12.3 (VIN+)
MISO: ISP1.1 (MISO), U$1.8 (PA5)
unnamed: C5.2, Q3.2 (S), U$5.2 (GND)
unnamed: C13.1, R15.2, U$12.4 (VIN-)
unnamed: R15.1, R16.1, U$9.CATHODE (C)
unnamed: R17.1, R18.1, U$10.C
unnamed: C14.1, R17.2, U$11.4 (VIN-)
unnamed: C16.1, R19.2
unnamed: C15.1, R20.2
SCL: ADS1115.10 (SCL), J2.1, U$1.6 (PA7), U$2.5 (SCL), U$3.3 (SCL)
SCL_EXT: ISP1.3 (SCK), Q2.2 (S), R10.1, U$1.9 (PA4)
SCL_EXT_HV: J1.1, J3.1, J4.1, Q2.3 (D), R11.1
SDA: ADS1115.9 (SDA), J2.2, U$1.5 (PB2), U$2.2 (SDA), U$3.2 (SDA)
SDA_EXT: ISP1.4 (MOSI), Q1.2 (S), R8.1, U$1.7 (PA6)
SDA_EXT_HV: J1.2, J3.2, J4.2, Q1.3 (D), R9.1
VIN+: C5.1, ISP1.2 (VCC), J1.3, J3.3, J4.3, Q3.1 (G), R9.2, R11.2, U$5.4 (VIN)
VIN-: J1.4, Q3.3 (D)

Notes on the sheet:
Software I2C
ADR = 0x48
ADR = 0x10
ADR = 0x49
Increase capacitive value?
Digital
Sensors
Power
Analog
Short Wave IR
Mid Wave IR
Connectors
Main Conn
Aux Conn
Parellel Headers

Board: 2 copper layers, 44 parts (0 on the bottom side), 24 nets, no tracks yet.

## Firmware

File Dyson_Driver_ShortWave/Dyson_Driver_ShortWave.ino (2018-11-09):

//Dyson_Driver_ShortWave.ino
#include "SlowSoftI2CMaster.h"
#include "WireS.h"
// #include <EEPROM.h> //DEBUG!
//Commands
#define CONF_CMD 0x00
#define ALS_CMD 0x04
#define WHITE_CMD 0x05

#define UVA_CMD 0x07
#define UVB_CMD 0x09
#define COMP1_CMD 0x0A
#define COMP2_CMD 0x0B

#define ADC_CONF 0x01
#define ADC_CONV 0x00
#define ADC0 0x4200
#define ADC1 0x5200
#define ADC2 0x6200
#define ADC3 0x7200

#define VIS_ADR 0x48
#define UV_ADR 0x10
#define ADC_ADR 0x49

#define READ 0x01
#define WRITE 0x00

#define BUF_LENGTH 64 //Length of I2C Buffer, verify with documentation 

#define LOW_LIM_VIS 10000  //Lower limit to the auto ranging of the VEML6030
#define HIGH_LIM_VIS 55000 //Upper limit to the auto ranging of the VEML6030

#define ADR_SEL_PIN 7 //Digital pin 7 is used to test which device address should be used
// #define ADR_ALT 0x41 //Alternative device address

//Global values for gain and int time of visable light sensor
uint8_t Gain = 0;
unsigned int IntTime = 0;
uint8_t GainValsVis[4] = {0b10, 0b11, 0b00, 0b01}; //Gain values for visible sensor
uint8_t GainsVis[4] = {1, 2, 8, 16}; //Gain multipliers for visable sensor 
uint8_t IntTimeValsVis[6] = {0b1100, 0b1000, 0b0000, 0b0001, 0b0010, 0b0011}; //Integration time values for visible sensor

//Compensation constants
float a = 1.92;
float b = 0.55;
float c = 2.46;
float d = 0.63;

volatile uint8_t ADR = 0x40; //Use arbitraty address, change using generall call??
const uint8_t ADR_Alt = 0x41; //Alternative device address  //WARNING! When a #define is used instead, problems are caused

unsigned int Config = 0; //Global config value

uint8_t Reg[26] = {0}; //Initialize registers
bool StartSample = true; //Flag used to start a new converstion, make a conversion on startup
const unsigned int UpdateRate = 5; //Rate of update

SlowSoftI2CMaster si = SlowSoftI2CMaster(PIN_B2, PIN_A7, true);  //Initialize software I2C

volatile bool StopFlag = false; //Used to indicate a stop condition 
volatile uint8_t RegID = 0; //Used to denote which register will be read from
volatile bool RepeatedStart = false; //Used to show if the start was repeated or not

void setup() {
  // Serial.begin(115200); //DEBUG!
  // Serial.println("begin"); //DEBUG!
  pinMode(ADR_SEL_PIN, INPUT_PULLUP);
  if(!digitalRead(ADR_SEL_PIN)) ADR = ADR_Alt; //If solder jumper is bridged, use alternate address //DEBUG!
  Wire.begin(ADR);  //Begin slave I2C
  // EEPROM.write(0, ADR);
  InitVEML(0x48); //Init Vis (VEML6030)
  InitVEML(0x10); //Init UV (VEML6075)
  InitADC(); //Init ADC (ADS1115)

  //Setup I2C slave
	Wire.onAddrReceive(addressEvent); // register event
	Wire.onRequest(requestEvent);     // register event
	Wire.onReceive(receiveEvent);
	Wire.onStop(stopEvent);

  si.i2c_init(); //Begin I2C master

  AutoRange_Vis(); //Auto range for given light conditions
}

void loop() {
	static unsigned int Count = 0; //Counter to determine update rate
	if(StartSample == true) {
		//Read new values in
		AutoRange_Vis();  //Run auto range
		delay(800); //Wait for new sample
		SplitAndLoad(0x0B, GetALS()); //Load ALS value
		SplitAndLoad(0x0D, GetWhite()); //Load white value
		SplitAndLoad(0x02, long(GetUV(0))); //Load UVA
		SplitAndLoad(0x07, long(GetUV(1))); //Load UVB
		SplitAndLoad(0x10, GetLuxGain()); //Load lux multiplier 
		SplitAndLoad(0x13, GetADC(0));
		SplitAndLoad(0x15, GetADC(1));
		SplitAndLoad(0x17, GetADC(2));

		StartSample = false; //Clear flag when new values updated  
	}
	if(Count++ == UpdateRate) {  //Fix update method??
		StartSample = true; //Set flag if number of updates have rolled over 
		Count = 0;
	}
	delay(100);
}

uint8_t InitVEML(uint8_t Adr) 
{
	uint8_t CMD = 0; 
	if(Adr == 0x48) CMD = 0x23;
	else CMD = 0;
    si.i2c_start((Adr << 1) | WRITE);
    si.i2c_write(0x00);
    si.i2c_write(0x00);
    si.i2c_write(CMD);
    si.i2c_stop(); 

    return 0; //Fix dummy
    //Setup gain and integration values manually! 
}

uint8_t InitADC() 
{
	//Setup ADC system 
	WriteWord_LE(ADC_ADR, ADC_CONF, ADC0); //Set to single shot mode with 
}

unsigned int GetADC(unsigned int Num)
{
	unsigned int ADC_Config = ADC0 | (Num << 12); //Use to select which ADC to get data from
	WriteWord_LE(ADC_ADR, ADC_CONF, ADC_Config); //Setup registers
	delay(300);  //Wait for next sample to be read
	return ReadWord_LE(ADC_ADR, ADC_CONV); //Read from register
}

float GetUV(uint8_t Sel) //Select A or B using Sel value (0 or 1) 
{
	float Comp1 = ReadWord(UV_ADR, COMP1_CMD);
	float Comp2 = ReadWord(UV_ADR, COMP2_CMD);

	float UV = 0;
	float UV_Comp = 0;
	if(Sel == 0) {
		UV = ReadWord(UV_ADR, UVA_CMD);
		UV_Comp = UV - a*Comp1 - b*Comp2;
		// Serial.println(UV);
	}

	if(Sel == 1) {
		UV = ReadWord(UV_ADR, UVB_CMD);
		UV_Comp = UV - c*Comp1 - d*Comp2;
	}

	return UV_Comp;
}

unsigned int GetALS() 
{
	return ReadWord(VIS_ADR, ALS_CMD);
}

unsigned int GetWhite() 
{
	return ReadWord(VIS_ADR, WHITE_CMD);
}

unsigned int GetLuxGain() 
{	//Add non-linear correction! 
	float GainTemp = float(Gain); //Hardcode max range for gain and int time 
	float IntTimeTemp = float(IntTime);  
	float Resolution = (1.8432/IntTimeTemp)/GainTemp;
	// unsigned int Resolution = (512/(IntTime/25.0))/(Gain/0.125);
	Serial.println(int(Resolution/0.0036)); //DEBUG!
	return int(Resolution/0.0036); //Return Lux scaler
}


uint8_t AutoRange_Vis() 
{	
	// WriteWord(VIS_ADR, CONF_CMD, (GainValsVis[0] << 11) | (IntTimeValsVis[0] << 6)); //Write min gain vals
	WriteWord(VIS_ADR, CONF_CMD, 0x1300);
	delay(800); //Wait for new sample
	unsigned int Val = GetALS();
	Serial.print("Val = "); Serial.println(Val); //DEBUG!
	// Serial.println(Val); //DEBUG!
	if(Val > HIGH_LIM_VIS) {
		Gain = GainsVis[0];  //Set global values
		IntTime = pow(2, 0); 
	}

	bool InRange = false; //Flag to test for range
	unsigned int ValTest = 0;
	uint8_t GainTemp = 0;  //Index of desired gain
	uint8_t IntTimeTemp = 0; //Index of desired integration time
	while(!InRange && IntTimeTemp < 6) {
		ValTest = (Val*int(GainsVis[GainTemp])*(1 << int(IntTimeTemp)));
		Serial.print("ValTest = "); Serial.println(ValTest); //DEBUG!
		if(ValTest < LOW_LIM_VIS) {
			GainTemp++;
		}
		if(GainTemp > 3 && IntTimeTemp < 5) {
			GainTemp = 0;
			IntTimeTemp++;
		}

		if(GainTemp == 3 && IntTimeTemp == 5) InRange = true; //Set if max value is reached 
		if(ValTest > LOW_LIM_VIS && ValTest < HIGH_LIM_VIS) InRange = true; //Found correct gain and int vals
	}
	Serial.print(GainValsVis[GainTemp], BIN); Serial.print("\t"); Serial.println(IntTimeValsVis[IntTimeTemp], BIN);  //DEBUG!
	WriteWord(VIS_ADR, CONF_CMD, (GainValsVis[GainTemp] << 11) | (IntTimeValsVis[IntTimeTemp] << 6));  //Write new gain value
	Gain = GainsVis[GainTemp];  //Set global values
	IntTime = pow(2, IntTimeTemp); 
}
// float GetGain(uint8_t GainBits)
// {
// 	uint8_t X0 = ReadBit(GainBits, 1);
// 	uint8_t X1 = ReadBit(GainBits, 0);
// 	Gain = pow(2, X0 - 3*X1);
// 	return Gain; 
// }

// unsigned int Gain2Bits(float GainVal)
// {
// 	for(int i = 0; i < 4; i++) {  //Use linear search to avoid float math and increase speed
// 		if(GainVals[i] == GainVal) {
// 			return (i << 11); //if entries match, return bits
// 		}
// 	}
// 	return 0x1000; //Return gain of 1/8 if not a valid gain value 
// }

// unsigned int GetIntTime()
// {
// 	Config = ReadWord(CONF_CMD); //Update global config value
// 	int X2X1 = (Config >> 6) & 0x03; 
// 	int X3 = ReadBit(Config, 8);
// 	int X4 = ReadBit(Config, 9);
// 	IntTime = 100*pow(2, X2X1)/pow(2, X3 + X4);  //Do some ugly math to go from bit pattern to value
// 	return IntTime; 
// }

// unsigned int IntTime2Bits(unsigned int Time)
// {
// 	uint8_t X2X1 = (int)(log(Time/100)/log(2));
// 	uint8_t X4X3 = (int)(((Time % 100) / 25) + 2*(Time % 50)/25);
// 	return ((X4X3 << 2) | (X2X1)) << 6; 
// }

// uint8_t SetGain(unsigned int GainVal)
// {
// 	Config = ReadWord(CONF_CMD); //Update global config value
// 	// Serial.print("Config = "); //DEBUG!
// 	// Serial.print(Config); //DEBUG! 
// 	// Serial.print(" "); //DEBUG!
// 	// Serial.println((Config & 0xE7FF) | GainVal); //DEBUG!
// 	return WriteConfig((Config & 0xE7FF) | GainVal);
// }

// uint8_t AutoRange()  //Automatically finds maximum gain and resolution values for given irradiance
// {
// 	// PowerSaveOff(); //Turn power save off for fastest reading
// 	SetIntTime(IT25); //Set to minimum integration time
// 	SetGain(GAIN_1_8); //Set to minmum gain
// 	// Serial.print("UnRanged Result ="); Serial.println(ReadWord(CONF_CMD), HEX); //DEBUG!
// 	// PowerOn();
// 	// long StartTime = millis(); //DEBUG! 
// 	// while(millis() - StartTime < 50) {  //DEBUG!
// 	// 	Serial.println(ReadWord(INT_CMD), HEX); //DEBUG!
// 	// }  //DEBUG!
// 	delay(30); //Wait for new sample
// 	float TestLux = GetLux(); //Get new lux value
// 	unsigned long HighLux = 120796;  //Start at max value
// 	unsigned int NewIntTime = 25; //Default to min value
// 	float NewGainHigh = 0.125; //Default to min value
// 	float NewGainLow = 0.25; //Default to 2nd lowest value
// 	float NewGain = 0.125; //Default to min value
// 	// Serial.print("LuxTest = "); //DEBUG!
// 	// Serial.println(TestLux); //DEBUG!
// 	//Increment through lux ranges to find desired gain range
// 	if(TestLux < 236) {  //If Lux is too small to measure at max values (<1.8432) or in minimum range, simply set to highest gain and integration time
// 		NewIntTime = 800;
// 		NewGain = 2;
// 	}
// 	else {  //If lux is not outside low range, search for a value
// 		for(int i = 0; i < 6; i++) {
// 			if(TestLux < HighLux && TestLux >= HighLux/2.0) {
// 				NewIntTime = NewIntTime * ceil(pow(2, i));
// 				break; //breakout of for loop since result is found
// 			}
// 			else HighLux = ceil(HighLux/2.0); //If not found, go to next lux range
// 		}

// 		if(TestLux < HighLux * 0.0625) NewGain = 2; //If below the lowest max for integration range, set to max gain
// 		else {  //Otherwise search for a new value 
// 			for(int g = 1; g < 3; g++) {
// 				if(TestLux < HighLux * (0.125/NewGainHigh) && TestLux >= HighLux * (0.125/NewGainLow)) {
// 					NewGain = NewGainHigh;
// 					break; //Break loop once gain is found
// 				}
// 				else {
// 					NewGainHigh = NewGainLow;
// 					NewGainLow = GetGain(GainValBits[g + 1]);
// 				}
// 			}
// 		}
// 	}

// 	// Serial.print("AutoRange Vals = "); Serial.print(NewGain); Serial.print(" "); Serial.println(NewIntTime); //DEBUG!
// 	unsigned int GainBits = Gain2Bits(NewGain); //Convert new gain value
// 	unsigned int IntBits = IntTime2Bits(NewIntTime); //Convert to new integration time
// 	// Serial.print("Bits = "); Serial.print(GainBits, HEX); Serial.print(" "); Serial.println(IntBits, HEX); //DEBUG!

// 	SetGain(GainBits);
// 	SetIntTime(IntBits);
// 	// Serial.print("AutoRanged Result ="); Serial.println(ReadWord(CONF_CMD), HEX); //DEBUG!
// }

// float GetGain()
// {
// 	Config = ReadWord(CONF_CMD); //Update global config value
// 	// Serial.println(Config); //DEBUG!
// 	int X0 = ReadBit(Config, 11);
// 	int X1 = ReadBit(Config, 12);
// 	Gain = pow(2, X0 - 3*X1);
// 	return Gain; 
// }

// unsigned int GetIntTime()
// {
// 	Config = ReadWord(CONF_CMD); //Update global config value
// 	int X2X1 = (Config >> 6) & 0x03; 
// 	int X3 = ReadBit(Config, 8);
// 	int X4 = ReadBit(Config, 9);
// 	IntTime = 100*pow(2, X2X1)/pow(2, X3 + X4);  //Do some ugly math to go from bit pattern to value
// 	return IntTime; 
// }

// float GetLux() 
// {	//Add non-linear correction! 
// 	GetGain(); //Update global values
// 	GetIntTime(); 
// 	float Resolution = (1.8432/((float)IntTime/25.0))*(0.125/Gain);
// 	// Serial.print("TEST = "); //DEBUG!
// 	// Serial.print(Resolution); //DEBUG!
// 	// Serial.print(" "); //DEBUG!
// 	// Serial.print(IntTime); //DEBUG! 
// 	// Serial.print(" "); //DEBUG!
// 	// Serial.println(Gain); //DEBUG!
// 	return GetALS()*Resolution; //Return scaled Lux mesurment
// }

// uint8_t ReadBit(unsigned int Data, uint8_t Pos)
// {
// 	return (Data >> Pos) & 0x01; 
// }
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

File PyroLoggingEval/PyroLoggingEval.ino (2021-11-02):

#include "Wire.h"
#include "math.h"
#include <SPI.h>
#include <SdFat.h>
#include <MCP3421.h>
#include <DS3231_Logger.h>

#define UVA_ADR 0x02
#define UVB_ADR 0x06
#define ALS_ADR 0x0B
#define WHITE_ADR 0x0D
#define LUXMUL_ADR 0x10
#define IR_MID_ADR 0x13
#define IR_SHORT_ADR 0x15
#define THERM_ADR 0x17

#define XAXIS 0x32
#define YAXIS 0x34
#define ZAXIS 0x36

#define ADR 0x40  //Address of Pyranometer
#define ACCEL_ADR 0x1D //Address of accelerometer (ADXL343)

const uint8_t RedLED = 13;
const uint8_t GreenLED = 15;
const uint8_t BlueLED = 14;

const uint8_t BuiltInLED = 20;

const unsigned long RED = 0xFFFF0000L;
const unsigned long GREEN = 0xFF00FF00L;
const unsigned long BLUE = 0xFF0000FFL;
const unsigned long MAROON = 0xFF800000L;
const unsigned long GOLD = 0xFFFFD700L;
const unsigned long ORANGE = 0xFFFFA500L;
const unsigned long PURPLE = 0xFF800080L;
const unsigned long CYAN = 0xFF00FFFF;
const unsigned long BLACK_ALERT = 0x802019FF;
const unsigned long OFF = 0x00;

const float LuxRes = 0.0036; //Min resolution of lux measurement

const float KippAndZonenConv = 1.257e-5; // [V/W/m^2] for a given kipp and zonen pyranometer 

const float A = 0.003354016;
const float B = 0.0003074038;
const float C = 1.019153E-05;
const float D = 9.093712E-07;

////////////////////////////////////SD////////////////////////////////////////
const int SD_CS = 4;
char FileNameC[11]; //Used for file handling
char FileNameTestC[11]; //Used for file handling
boolean SD_Init = false;
const uint8_t SD_CD = 1;
SdFat SD;
byte  keep_SPCR;

////////////////////////////////////CLOCK//////////////////////////////////////
DS3231_Logger RTC;

MCP3421 adc;

String LogTimeDate = "2063/04/05 20:00:00";

const int Ext3v3Ctrl = 19; 

bool GlobalError = false;

void setup() {
	// put your setup code here, to run once:
	pinMode(Ext3v3Ctrl, OUTPUT);
  	digitalWrite(Ext3v3Ctrl, LOW); //Turn on power by default, turn off later to sleep

  	pinMode(RedLED, OUTPUT);
	pinMode(GreenLED, OUTPUT);
	pinMode(BlueLED, OUTPUT);
	pinMode(BuiltInLED, OUTPUT);
	LED_Color(OFF); //Turn off intially 

	digitalWrite(BuiltInLED, LOW); //Turn LED On

	Serial.begin(115200); 
	Serial.println("Welcome to the Sphere...");
	Wire.begin();
	RTC.Begin(); //Initalize RTC
	InitAccel();
	adc.Begin();
	adc.SetResolution(18);
	// adc.SetGain(8);
	// SD.begin(SD_CS);
	pinMode(SD_CS, OUTPUT);
	SDTest();
	InitLogFile();

	digitalWrite(BuiltInLED, HIGH); //Turn LED off
	if(GlobalError == false) LED_Color(GREEN);
	else LED_Color(RED);
	delay(2000);
	LED_Color(OFF);

}


void loop() {
  // put your main code here, to run repeatedly:
  GetTime(); //FIX!
  String Data = String(GetUVA()) + "," + String(GetUVB()) + "," + String(GetALS()) + "," + String(GetWhite()) + "," + String(GetLux()) + "," + String(GetIR_Short()) + "," + String(GetIR_Mid()) + "," + String(GetWatts()) + "," + String(GetAngle(3)) + "," + String(GetAngle(4)) + "," + LogTimeDate;
  LogStr(Data);
  Serial.println(LogTimeDate);
  delay(1000);
}
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

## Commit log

2018-06-05 Rebuild repo
    Previous repo was borked due to inclusion of large peripheral files from LTSpice simulations, repo is now being rebuild with changes to gitignore in order to prevent issues like this in the future
    [Apogee_SP110_Response.csv, IR_LongWave_Response.csv, IR_MidWave_Response.csv, IR_ShortWave_Response.csv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]
2018-06-05 Made fixes to #2, #3, #4
    Fixed the silk screen numbering issue, fixed pinout of thermopile, connected voltage ref pin
    [LongWaveModule.brd, LongWaveModule.sch]
2018-06-07 Added sub-alpha firmware
    I2C firmware used for translating I2C commands and readdressing (currently not functional), driver firmware is used as a true sensor interface to read from sub-slaves and populate registers (currentl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
2018-06-19 Improved firmware to include auto ranging
    Also added logging software ALPHA revision
    [LongWaveModule_BOM.csv, ShortWaveModule_BOM.csv, ShortWaveModule_SmallBoard.brd, ShortWaveModule_SmallBoard.sch]
2018-06-27 Added pullups to shortwave module
    Added pullups to onboard I2C on shortwave module, still need to fix silk screen and update parts before ready to ship
    [ShortWaveModule_SmallBoard.brd, ShortWaveModule_SmallBoard.sch]
2018-06-28 Updated parts and BOM
    [ShortWaveModule_BOM.csv, ShortWaveModule_SmallBoard.brd, ShortWaveModule_SmallBoard.sch]
2018-06-28 Updated part info, license and BOM
    [LongWaveModule.brd, LongWaveModule.sch, LongWaveModule_BOM.csv, ShortWaveModule_SmallBoard.brd]
2018-06-28 Generated gerbers for Mrk 0.1
    Added Gerbers for Mrk 0.1 revision, fixed silk screen issues, added pullup resistors for on board I2C on shortwave module, and changed amplifiers on longwave module (eliminated use of LTC2054HV, and 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
    [LongWaveModule.brd, LongWaveModule.sch, LongWaveModule_BOM.csv, ShortWaveModule_BOM.csv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]
2018-07-10 Added mechanical parts and updated gerbers and ref designators
    Updated gerbers for long wave and fixed reference designators for short wave
    [BoardCaseMount.SLDPRT, BoardCaseMount.STL, LongWaveMountPlate.SLDPRT, LongWaveMountPlate.STL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]
2018-07-17 Added solder stencil DXF
    [LongWaveModule-bcream.dxf, LongWaveModule-tcream.dxf, Stencil.dxf]
2018-07-21 Added pipe mount assembly
    [PipeMount.SLDASM]
2018-11-09 Added pin descriptors for Dyson v0.1
2018-11-09 Updated SW firmware, fixed ADR issue
    Updated Dyson shortwave firmware to fix alternative ADR setting issue. Also removed some stale debug statements and changed default flag to log when power is first applied to device in order to work 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
2018-11-09 Updated case mount to allow for pins to not clash
    added cutout to allow for clearance of backside of pins
    [BoardCaseMount.SLDPRT, BoardCaseMount.STL]
2018-11-09 Added cutouts in mount
    Added cutouts for ICSP headers to allow board to lay flat on mount
    [BoardCaseMount.SLDPRT, BoardCaseMount.STL]
2018-11-27 Added response curves for LW
    Added response curves for longwave sensor, and fitting info for thermistor on LW
    [ZTP-135_Response.csv, ZTP-135_ThermistorFit.csv]
2018-11-29 Added mechanical parts
    Added placement guides and drill guide
    [DiffuserGuide_BOTTOM.SLDPRT, DiffuserGuide_BOTTOM.STL, DiffuserGuide_TOP.SLDPRT, DiffuserGuide_TOP.STL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]
2018-11-29 Added mechanical designs and reg map
    Added new mechanical designs along with a preliminary register map, continued expansion to come
    [LongWaveModule.brd, LongWaveMountPlate_v1.SLDPRT, LongWaveMountPlate_v1.STL, WP-31_InternalMountPlate.SLDPRT]
2018-12-01 Updated firmware
    Fixed update timing issue, need to remove digital pin debug statements!
2018-12-12 Added SW mount w/desiccant holders
    Added a new version of the board holder for the short wave unit, with spaces for holding desiccant that will not allow it to move around in the box and cause problems
    [BoardCaseMount_DesicantHolders.SLDPRT, BoardCaseMount_DesicantHolders.STL]
2018-12-13 Added SW mount w/desiccant holders
    [BoardCaseMount_DesicantHolders.SLDPRT, BoardCaseMount_DesicantHolders.STL]
2018-12-15 Added pipe mount cutout shape
    [PipeMount_Outline.DXF]
2019-01-14 Fixed crash in Board Mount
    The pins of the bottom header would crash with the body of the BoardCaseMount, this was fixed with an cutout in `BoardCaseMount_DesicantHolder.SLDPRT`. Also updated`.stl` and generated bulk GCode to 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
    [BoardCaseMount_DesicantHolders.SLDPRT, BoardCaseMount_DesicantHolders.STL]
2019-05-21 Added experimental high speed/low power firmware
2020-05-27 Design files
    [PyroTestingBoard.SLDPRT, PyroTestingBoard.STEP, PyroTestingBoard.STL, PyroTestingPlate.DXF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]
2020-05-27 Easel pipe mount
2020-05-27 Millable components and U bolt sizes
2021-11-02 Dyson-->Monarch, aside from Eagle files & co
    [StencilMount_MonarchLW.SLDPRT, StencilMount_MonarchLW.STL]
2021-11-03 Dyson --> Monarch in sch and on silk
    [LongWaveModule.brd, LongWaveModule.sch, ShortWaveModule_SmallBoard.brd, ShortWaveModule_SmallBoard.sch]

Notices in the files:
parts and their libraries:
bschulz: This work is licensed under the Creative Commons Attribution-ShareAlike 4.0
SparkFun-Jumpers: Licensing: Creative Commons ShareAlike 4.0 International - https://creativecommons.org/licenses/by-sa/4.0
